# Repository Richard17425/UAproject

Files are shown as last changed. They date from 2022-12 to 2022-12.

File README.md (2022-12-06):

# **UAproject** (ReadOnly)
These are the projects I was responsible for when I was in University of Alberta, summer 2022. 
The projects this folder include are:

-  ## [**Cane**](Cane/scirobotics.abg6594_sm.pdf) 
-  ## [**Motion Sensor Glove**](Motion%20Sensor%20Glove/Instruction.pdf)
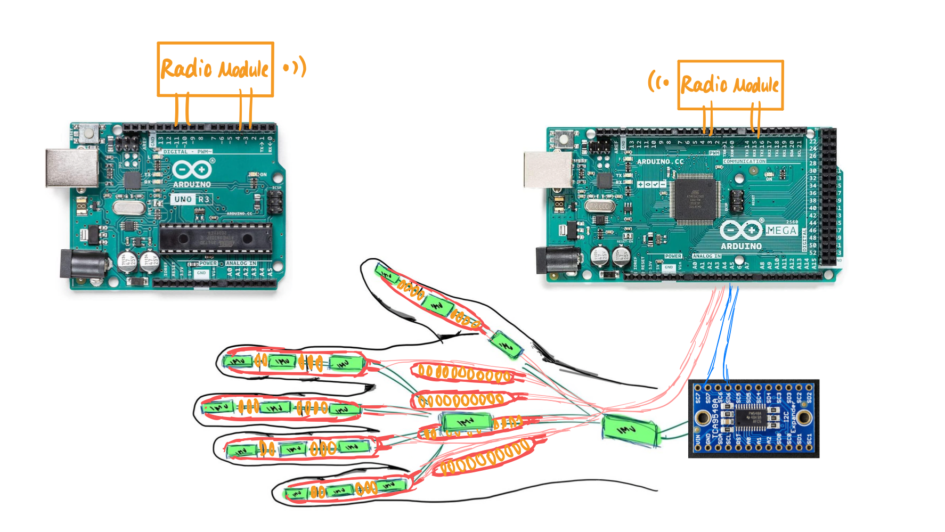
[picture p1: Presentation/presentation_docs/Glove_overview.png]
glove
  
-  ## [**Prosthetic Hand**](Prosthetic%20Hand/06_01_22_abstract-presentation.pdf)
hand

You can find details of these project in the folders.

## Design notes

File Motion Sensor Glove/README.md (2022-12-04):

# **Motion Sensor Glove**

This is the finnal vision of this project.So it will be much more simplified.

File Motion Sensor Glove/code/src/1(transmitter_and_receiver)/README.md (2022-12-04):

**Module 1**
====================================
This code contains transmitter and receiver codes
-----------------

    Make sure you have moved the *SparkFun_LSM9DS1_Arduino_Library folder* and the *RadioHead* into a libraries folder within your Arduino sketchbook or use the Library Manger to install.

- Receiver_Code_V2.0* should be uploaded to the Arduino Uno. Baud rate is **9 600**.

- *Receiver_Code_V2.0* should be uploaded to the Aduino Mega2560. Baud rate is **115 200**.

Author: richy70425@gmail.com

Original Creation Date: September, 2022

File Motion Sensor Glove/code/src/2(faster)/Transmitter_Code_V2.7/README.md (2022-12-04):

**Module 2**
====================================
This code contains only transmitter code, which means we connect the transmitter(Arduino Mega2560) to laptop directly.
-----------------

    Make sure you have moved the *SparkFun_LSM9DS1_Arduino_Library folder* and the *RadioHead* into a libraries folder within your Arduino sketchbook or use the Library Manger to install.

- *Transmitter_Code_V2.7* should be uploaded to the Arduino Uno. Baud rate is **2000 00**.

Author: richy70425@gmail.com

Original Creation Date: September, 2022

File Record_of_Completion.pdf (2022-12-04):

## Record of Completion

This certificate hereby acknowledges that

## Lab & Chemical Safety 2021

## Ruiqi Mao

has completed the course

July 13, 2022

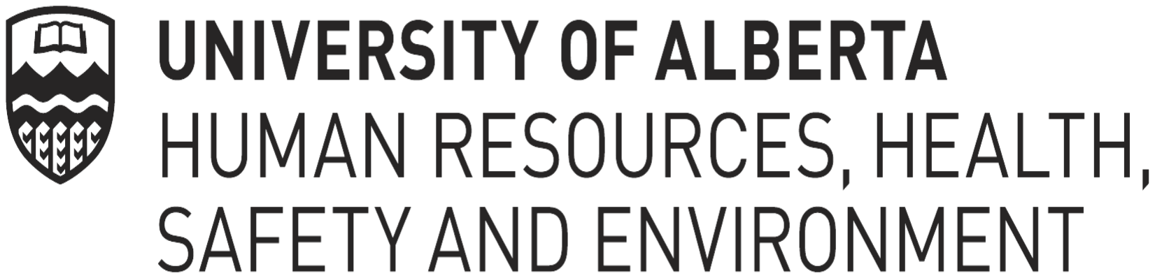
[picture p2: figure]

Philip Stack
Director, Health, Safety & Environment | 4lxVLtbr6s

Powered by TCPDF (www.tcpdf.org)

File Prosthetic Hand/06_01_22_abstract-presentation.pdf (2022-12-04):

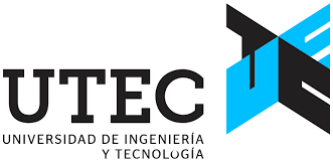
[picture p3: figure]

# DEVELOPMENT OF A LOW-COST

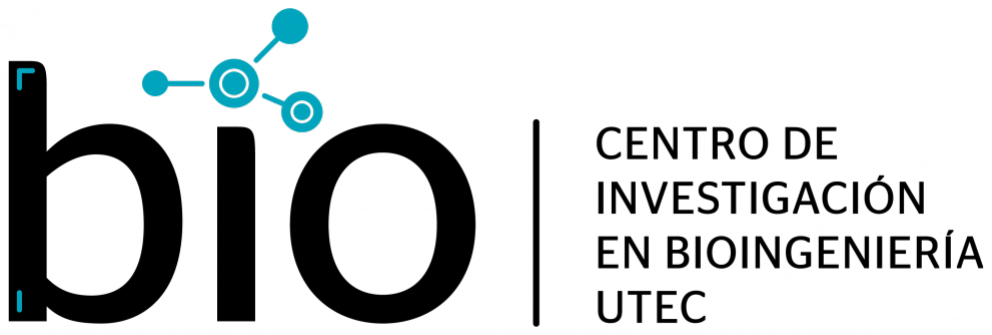
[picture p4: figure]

# LIGHTWEIGHT EMG-CONTROLLED TRANSRADIAL

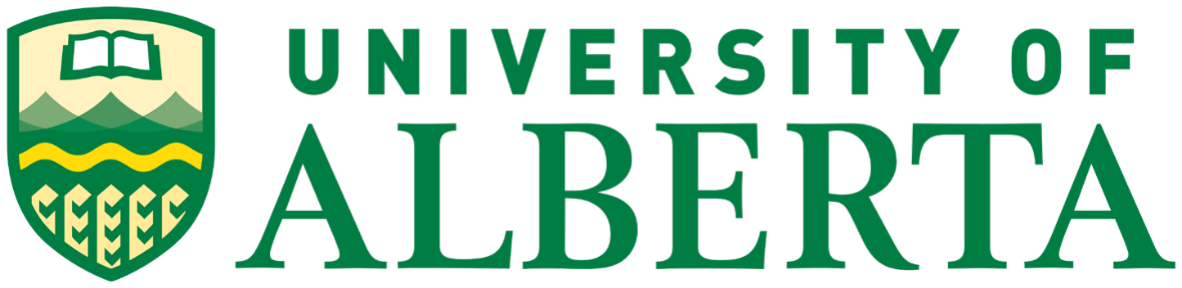
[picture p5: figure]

# PROSTHESIS

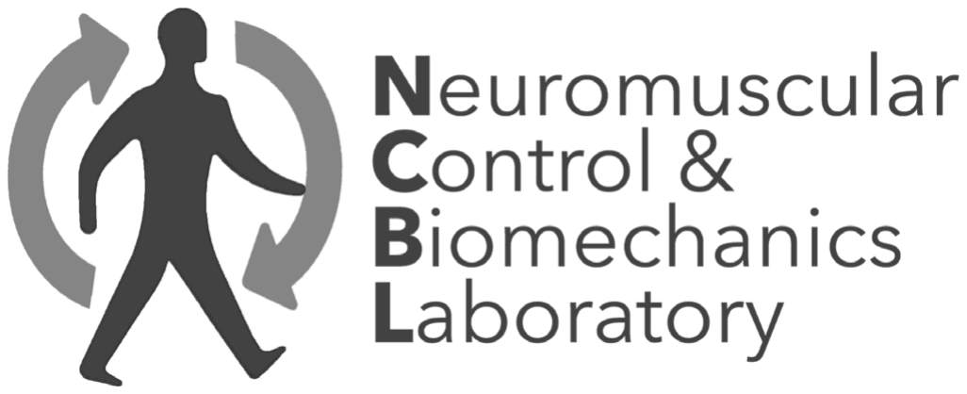
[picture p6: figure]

# Leonardo Torres Oscar Ramos, PhD | Hossein Rouhani, PhD

# Motivation

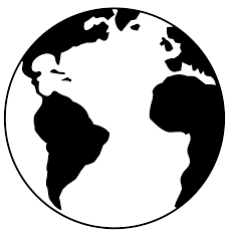
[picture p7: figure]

## 0.5% of population need orthotic and prosthetic services

### 35-40M of people

(WHO, 2017) [1]

## 85-95% of people in need of

an orthopedic device such as a prosthesis or orthosis, don’t have access to those
(WHO, 2017) [1]

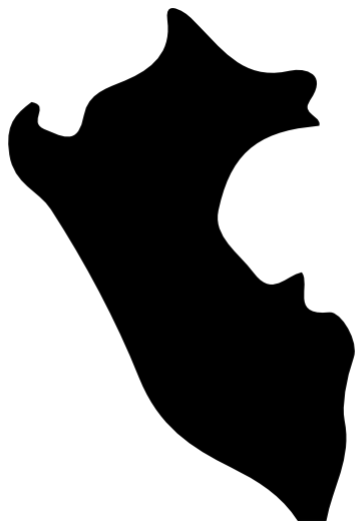
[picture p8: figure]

## 1.57% Peruvians with arm or leg disability

(National Census - INEI, 2017) [2]

## 0.001% Peruvians with locomotion disability use a prosthetic arm

(National Survey Specialized on Disability - INEI, 2012) [3]
2

# Motivation

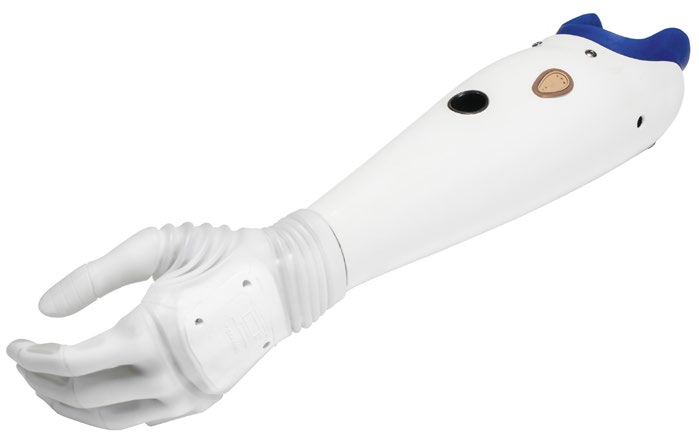
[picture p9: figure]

3

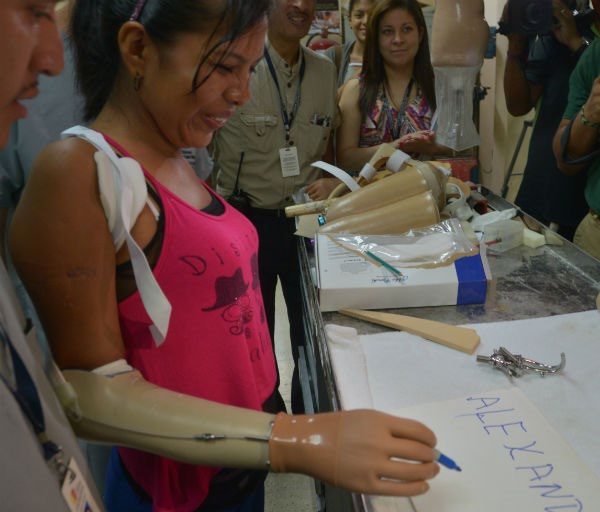
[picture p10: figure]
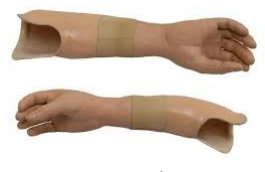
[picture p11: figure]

## Prosthesis from the National Rehabilitation Institute (INR), Peru

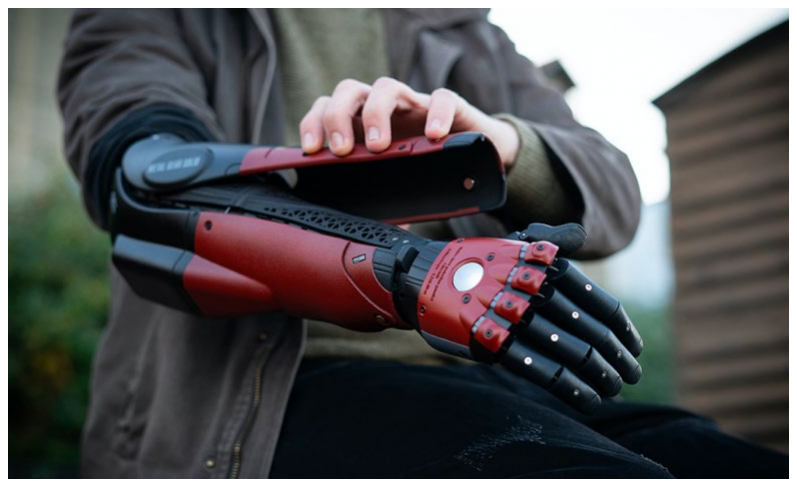
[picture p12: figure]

## Myoelectric Prosthesis from International Market

### Mechanical prosthesis Price: $ 1.500 USD [4]

### Aesthetic prosthesis Price: $ 1.000 USD [5]

### Hero Arm Prosthesis, Open Bionics. Price: $ 6.600 USD

[6]

### Michelangelo Hand

Prosthesis, Ottobock.

### Price: $ 60.000 USD

[6]

# Justification

4

## Accessibility: less cost of implementation

## Open source: easy replication by maker community

## Functional: actuation system with myoelectric signal

## Scalability: fast updates with software

# Objectives

5

Design the anthropomorphic prosthesis with 3 degrees of freedom.

Design the electronic system of the prosthesis.

## Develop the control system of the prosthesis using myoelectric signal

classification.

## Build the prototype of the upper limb prosthesis from the designed

components.

Functionally validate the implemented prosthesis.

# Mechanical design: SolidWorks assembly

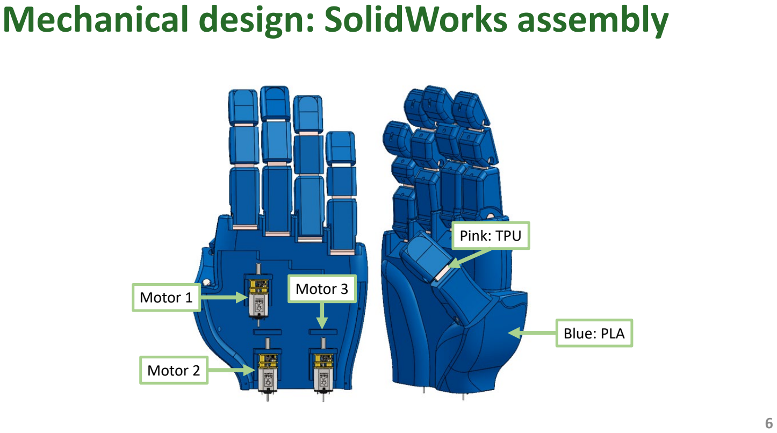
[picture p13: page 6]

6

### Motor 1

### Motor 2

### Motor 3

### Pink: TPU

### Blue: PLA

# Mechanical design: based on anthropometric data

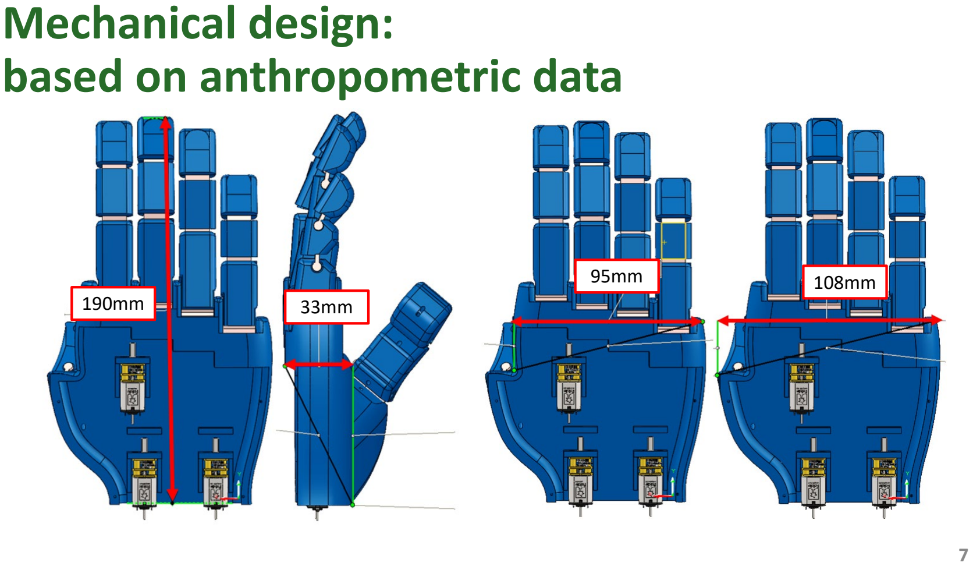
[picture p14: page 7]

7

190mm | 33mm
95mm | 108mm

# Electronic system: circuit diagram

8

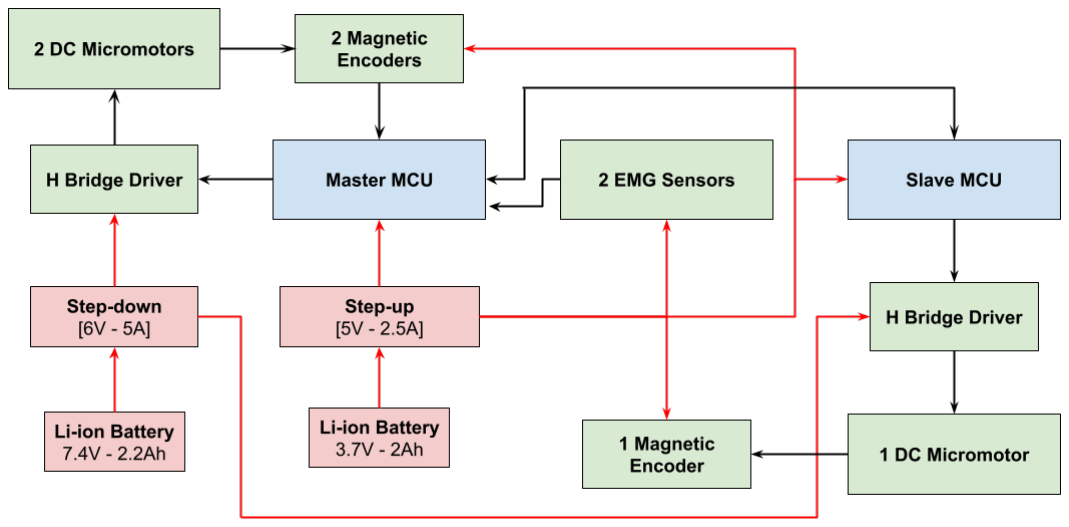
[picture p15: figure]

## LEGEND

### Microcontroller

### Power Supply

### Sensor/Actuator

# Electronic system: final circuit

## Printed circuit board (PCB) assembly results:

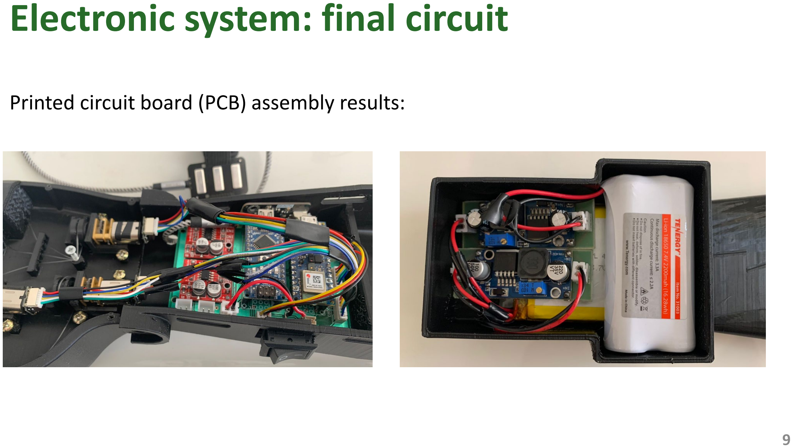
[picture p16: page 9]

9

# EMG signal: Processing Algorithm

10

### Data collection of EMG sensor

### Data filtering

### Data storage for 0.5s

### Calculation of average data

Changes state | Remains in the same state Threshold exceeded?
Yes | No

# Control System: Block diagram

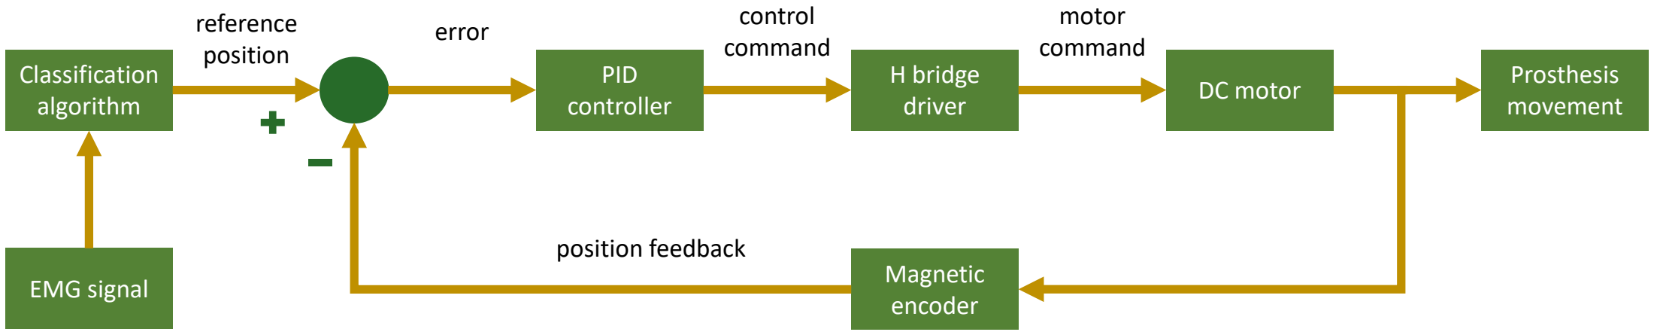
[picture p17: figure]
EMG signal; Classification algorithm; PID controller; H bridge; driver; DC motor; Prosthesis; movement; reference position; error; control command; motor command; Magnetic encoder; position feedback

11

# Fabrication: final cost of prosthesis

12

Service | Quantity | Unit Price | Cost
3D printing | 65 hours | $ 2.00 | $ 130.00
PCB printing | 1 unit | $ 35.00 | $ 35.00
| | Total | $ 165.00
Material costs | $ 274.75
Service costs | $ 165.00
Total | ≈ $ 440.00

# Weight of the prosthesis

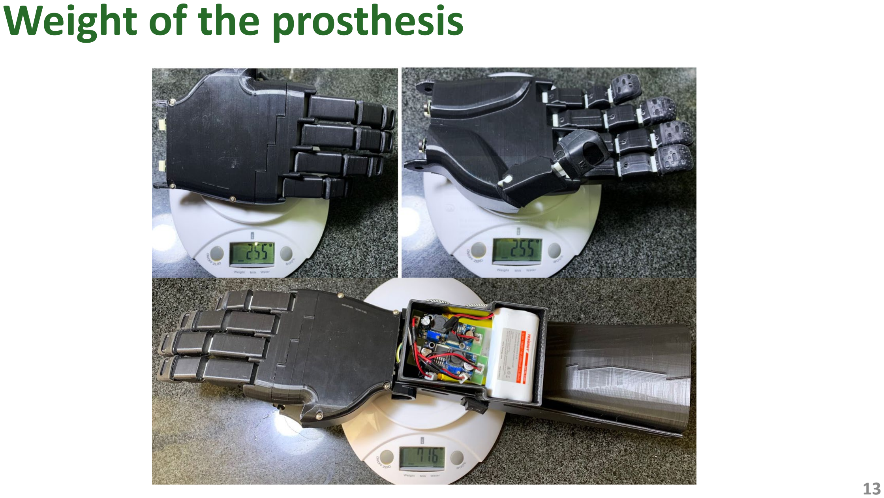
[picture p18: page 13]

13

Figure 18. Weight of the assembled prosthetic hand.

# Prosthetic hand movement

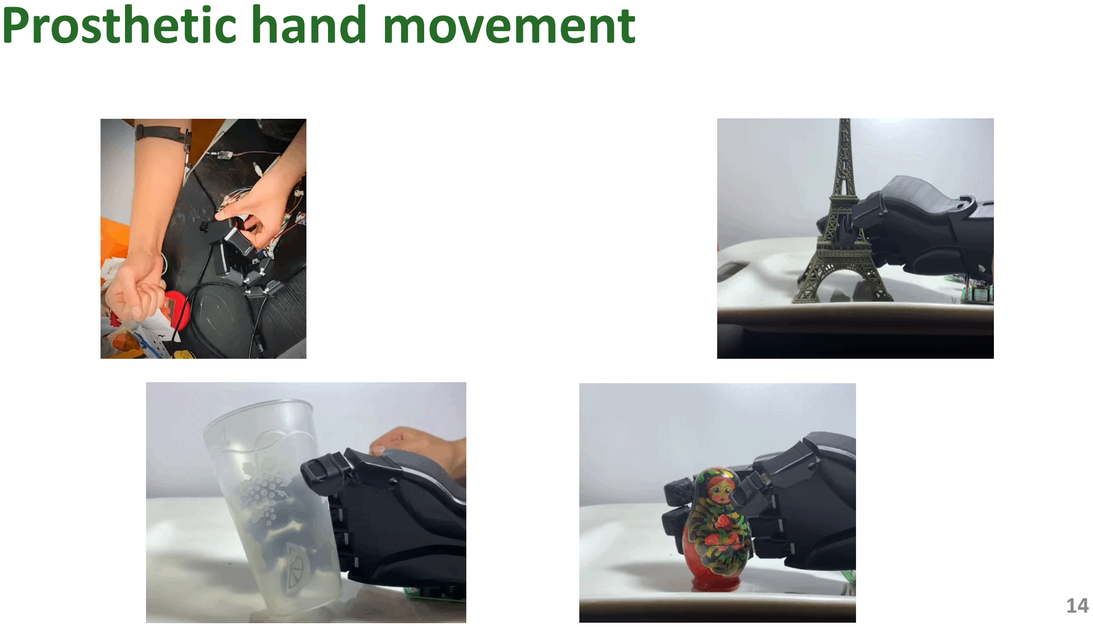
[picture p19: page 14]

14

# Conclusion:

- CAD design of the anthropomorphic prosthesis with 3 degrees of freedom.

## - Hand design similar to the average anthropometric measurements of the Latin

American database.
- Prototyping: 3D Printing time of 65 hours.
- Final implementation cost for materials and service was $440.
- Total weight within the limits initially proposed: 716 grams.

15

# Bibliography

16

[1] Organización Mundial de la Salud, “Normas de Ortoprostésica Parte 1: Normas,” 2017.
[2] Instituto Nacional de Estadística e Informática del Perú (INEI), “Perfil sociodemográfico de la población con discapacidad, 2017,” 2017.
[3] INEI, “Primera Encuesta Nacional Especializada sobre Discapacidad 2012,” 2012.
[4] Instituto Nacional de Rehabilitación, Resolución Directoral 122-2015-SA-DG-INR. Perú, 2015.
[5] Instituto Nacional de Rehabilitación, Resolución Directoral 406-2015-SA-DG-INR. 2015.
[6] A. Calado, F. Soares, and D. Matos, “A Review on Commercially Available Anthropomorphic Myoelectric Prosthetic Hands, Pattern-Recognition-Based Microcontrollers and sEMG Sensors used for Prosthetic Control,” 19th IEEE Int. Conf. Auton. Robot Syst. Compet. ICARSC 2019, 2019, doi: 10.1109/ICARSC.2019.8733629.
[7] Open Bionics, “Meet the Hero Arm – a prosthetic arm for adults and childern”, 2021. https://openbionics.com/hero-arm/ (accessed Aug. 5, 2021).
[8] R. Ávila, P. Lilia, and G. Elvia, Dimensiones antropométricas de población latinoamericana. 2007.
[9] O. Binvignat, A. Almagià, P. Lizana, and E. Olave, “Aspectos Biométricos de la Mano de Individuos Chilenos,” Int. J. Morphol., vol. 30, no. 2, pp. 599–606, 2012, doi: 10.4067/s0717-95022012000200040.
[10] B. Hirt, H. Seyhan, M. Wagner, and R. Zumhasch, Hand and Wrist Anatomy and Biomechanics: A Comprehensive Guide. Stuttgart: Thieme, 2017.

# Follow us on:

# THANK YOU !

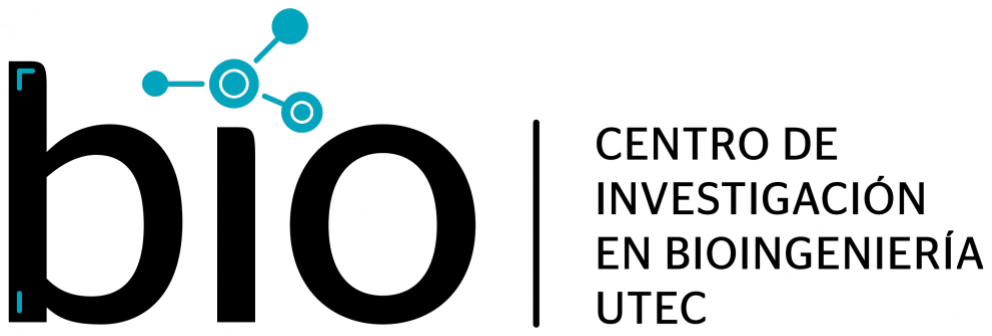
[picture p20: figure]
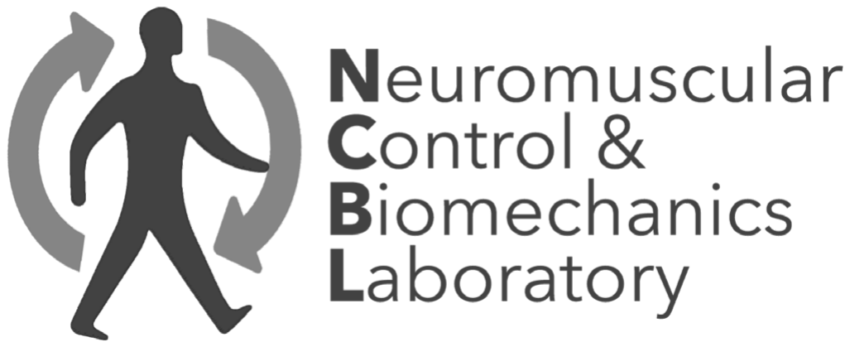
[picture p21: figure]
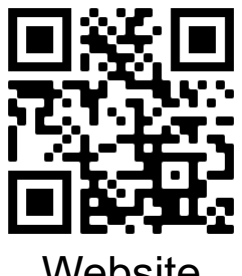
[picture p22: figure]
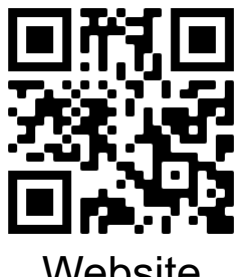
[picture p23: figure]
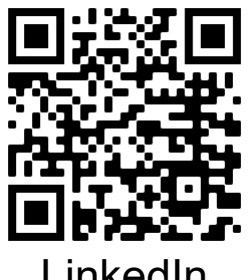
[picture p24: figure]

Website | LinkedIn | Website

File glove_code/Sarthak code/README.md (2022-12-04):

# These are Sarthak‘s codes
Version 2.0 is my improved code

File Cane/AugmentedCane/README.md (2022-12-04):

# AugmentedCane


The Augmented Cane project improves the mobility of people with impaired vision by using cutting-edge robotics. Read the full research paper: https://www.science.org/doi/10.1126/scirobotics.abg6594

If you use a part of this project please cite our work: P. Slade, A. Tambe, M. J. Kochenderfer, Multimodal sensing and intuitive steering assistance improve navigation and mobility for people with impaired vision. Sci. Robot. 6, eabg6594 (2021).

The Augmented Cane project is completely open-source. To build your own copy check out the cane_assembly document with instructions on replicating the device. The image of the Raspberry Pi used is available in a separate repository due to its size: https://doi.org/10.5281/zenodo.5508346

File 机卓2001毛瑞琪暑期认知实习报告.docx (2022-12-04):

2022暑期认知实习报告

机卓2001毛瑞琪

今年暑假，我有幸能参加由中国留学基金委资助的与加拿大阿尔伯塔大学的为期三个月的暑期实习项目。

阿尔伯塔大学（University of Alberta），简称“UA”，始建于1908年，是坐落于加拿大阿尔伯塔省会埃德蒙顿的一所世界著名研究型大学，是加拿大U15研究型大学联盟创始成员、世界大学联盟成员以及世界能源大学联盟成员。阿尔伯塔大学是加拿大最大的研究型大学之一，在地球科学，石油化工、化学、商学、农学、生物医学等学科最为著名。阿尔伯塔大学校友包含第16任加拿大总理，三位诺贝尔奖得主（包括2020年诺贝尔生理学医学奖得主霍顿 ），75位罗德学者（总数居世界名牌大学前列），141位加拿大皇家学会成员，111位加拿大首席研究教授。

阿尔伯塔大学的人工智能专业在全球居于领先地位，全球顶级计算机科学机构排名CSRankings 2010-2020年度人工智能领域世界排名第37名，其中人工智能和机器学习世界第6名。强化学习之父Rich Sutton、以及Alpha Go的主要作者大卫·席尔瓦（David Silver）和黄士杰（Aja Huang）均来自阿尔伯塔大学。

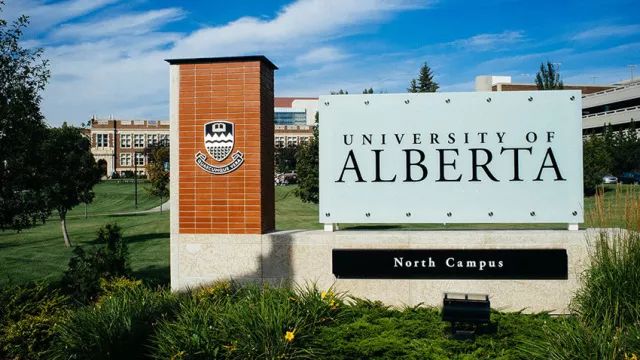
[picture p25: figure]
查看源图像

关于阿尔伯塔大学的机械工程系，教授告诉我，这里主要想要为学生提供在加拿大最大的机械工程系追求卓越、高质量教育的机会。学院的1,450名学生（1000 名本科生和450名研究生）在蓬勃发展和充满活力的环境中学习，强调扎实的学术和良好的实践技能。机械学院还提供合作的本科课程（包括生物医学合作选项），以及工程硕士、理学硕士和博士研究生课程。

我还了解到，阿尔伯塔大学的学生有许多丰富的研究和课外机会：从本科生研究计划到许多专注于机器人技术、自主飞行、F-1 赛车、火箭、生物力学、卫星、永续农业、氢动力汽车和许多其他领域的学生俱乐部团体，每个学生都会对某些事情或者某项研究充满热情。

在侧边栏查询中搜索

我从前觉得自己总是很忙，有各种各样学业的任务需要完成，一直在学习着、了解着工程与机械相关的内容，查论文写报告做展示，但在投入到实际中去探索与了解的时间确实有些捉襟见肘。真的说到未来科研或者工作会需要做些什么，我自己很难给出明确的回答。直到这次出来实习，才开始考虑一些之前没有重视的问题，开始真正去思考关于自己未来的事情。

首先是这边的科研，阿尔伯塔大学机械工程学院的主要研究大概可以分为下面四个方面：

设计理论与方法论：协作和交互方法；设计内容和流程管理；跨学科设计整合与优化；DFX; 功能建模；以用户为中心的设计建模。

设计和制造信息学：计算机辅助设计（CAD）；计算机辅助制造（CAM）；消费品创新；工程信息集成；工业管理信息学；知识工程；坚固的设计；产品生命周期管理；智能规划。

制造与生产系统设计与自动化：添加剂制造; 自动化和机器人技术；计算机数控（CNC）；柔性制造系统（FMS）；混合制造；STEP-NC，异种材料的激光焊接；物理、功能、工具和生产模型集成；和制造工装设计。

制造工艺优化：组装/拆卸；企业资源计划（ERP）系统的定制和开发；制造业供应链的扩展；人机协作；工业信息交互的互操作性；精益制造；工程设计、制造和生产过程的优化；制造质量保证；制造过程的模拟和分析；公差分析和分配。

因为这次的暑期实习项目是导师制的，所以我的大部分工作都是在完成导师的给我分配的项目任务。刚开始进入课题项目的时候我还只是做一些比较简单基础的工作，像是采购完成项目需要用到的一些材料跟零件，焊一些传感器的引脚以及做一些调试测试，作为志愿者完成实验室师兄师姐们的课题实验。这一系列的工作和任务让我对这边的科研环境与氛围有了基本的了解——一位在这边做科研的中国博士师兄告诉我，这边实验室的工作氛围比较自由，可以自己安排每天在实验室的工作时间，当然也可以居家办公，这就给了我们很高的自主安排的空间。当然，随之而来的也是对自己自律性的考验。我觉得这样安排的好处在于可以让那些真正想做科研的研究生们可以有一个安静的环境和氛围来做研究，每天自己计划要进行的任务和实验，不需要为刻板的工时去被迫强制性地工作，更多让人感受到的是在为自己打工。


后来我在实验室做的工作逐渐越来越多，也有了自己的主线任务。一个是拓展手的项目，原理是人在伸展或者握紧手的时候，实际上手臂上的韧带是会有相应的动作的，根据传感器得到的韧带的起伏数据，单片机就能知道我们手掌五指所要进行的动作是握拳或者是松手。这个项目的初衷是想要帮助那些残障人士在日常生活中能够像正常人一样拿东西，做一些简单的动作。为了保证假肢的制造精度和尽量还原出人手的各个关节形态，整个假手的制造主要是3D打印加上一些拼装，手指的韧带采用的是TPU材料，更加具有韧性。五个手指分别用三个电机来驱动，当单片机对传感器获得的手部的信号分析处理后，会向电机做出相应的指令，从而电机转动拉动绳子，实现手指的弯曲。整个原理其实很简单，但实现的过程却充满了艰辛和坎坷。由于要获得手部韧带准确的动作信息，传感器的位置跟方向都很讲究。所以对医学几乎一无所知的我在这上面吃了大亏。我上网到处搜索手臂韧带的相关信息，看了一些相关的论文研究，还加以自己的推测，一次又一次尝试，调整传感器在手臂上的粘贴位置，最终才让全部的四个传感器处在了正确的位置。经过后来又很多次的调试，才终于让整个的拓展手正常工作了起来。

这个项目我收获最大的除了一些经验，也让我学会在遇到困难的时候不畏惧不浮躁—如果只是抱怨是解决不了问题的，只有亲手去做，认真去思考才能真正解决问题。还有就是要细心。在调试电机的时候，我发现有一个电机总是对单片机发出的信号无动于衷，我反复检查了代码与连线，最后发现居然是驱动板上的GND没有接上。这些小错误都耗费了我很多的时间，也是给我了很好的教训。毕竟这还只是一个小项目，要是以后到了真正工程上的大项目，这样的粗心可是折腾不起的。因为自己的一个小小的粗心可能带来的是数以万计的损失和浪费，这真的是一个工程师要绝对避免的。


同时，关于这个项目，教授还让我思考是否还能对这个假肢做出一些改进，是否能够站在环境保护和可持续发展的角度，思考机械设计制造及其自动化领域工程实践的可持续发展性，并评价产品周期中可能对人类和环境造成的损害和隐患。这是我在开始时没有考虑到的，就像整个手臂的制造为了方便，我选择了PLA的塑料，但是却没有考虑到这后面的成本和环保问题。是否能够有更好的材料来进行替代，是否可以降低整个假肢的生产制造成本，我觉得这都是一个好的工程师在设计之初就应该考虑到的。我又想到原来在学校的时候听的院士的讲座上也提到了可持续发展的问题----我们国家人口多、自然资源短缺、经济基础和科技水平落后，只有节约资源、保护环境，才能实现社会和经济的良性循环，使各方面的发展能够持续有后劲。可持续发展要求我们 “能满足当代人的需要，又不对后代人满足其需要的能力构成危害的发展”。 它包括两个重要概念：一个是需要，尤其是世界各国人们的基本需要，应将此放在特别优先的地位来考虑；另一个是限制，技术状况和社会组织对环境满足眼前和将来需要的能力施加的限制。可持续发展的概念涵盖范围包括国际、区域、地方及特定界别的层面，是我们国家科学发展观的基本要求之一，也是当今世界关注的重点之一。原来总觉得这种事情仿佛是只出现在号召里，自己难能做些什么帮助，但确实仔细一想其实就在机械设计制造的过程中都有很多可以环保节能的可持续的设计和方法，有时候甚至是一个小小的改动或者改进，在大批量生产制造中都会产生举足轻重的作用。而且可持续发展更像是一种为人处世的哲学，它要求我们从注重眼前利益、局部利益的发展转向长期利益、整体利益的发展，需要我们拥有一种大局观和对未来的规划。


教授也告诉我，机械其实包含的领域很广，是一个多学科研究交叉互相融合的领域。一个好的机械工程师或者研究人员应该专注于系统、流程、机器、工具和生产设备的设计和开发，通过创造性的概念化、知识工程的工程化，找到最经济、最有效的方法，将想法转化为新的或更新的产品、流程或技术来满足社会和工业需求。这种研究工作通常需要考虑经济、安全、信息学以及环境、认知、文化、社会学甚至生理学问题，所以对我们的要求非常高。

教授虽然对于研究生的工作时间没有强制性的要求，可是对于我们的工作质量与成果却十分严格。每周，教授都安排师姐给我分配任务，师姐每天还会询问我的进度，如果有遇到困难或者需要就可以及时解决。教授一般出现在一周一次的组会上，有一次教授就师兄展示PPT上的一个点讨论了很久，因为觉得关于脑电波获取思路原理上没有讲得清楚正确而把师兄批评了一顿。还有一次，同样是交换在我们实验室进行项目实习的一位墨西哥的同学在进行最终的项目展示时，因为PPT里关于自己成果展示不够充分明显，导师也毫不留情地指出批评。但是尽管如此，我觉得难能可贵地是，教授依旧能跟我们打成一片。在八月初我们实验室的聚餐中，教授一手拿着汉堡，一边跟我们几个年轻的暑期实习生聊天。当时突然觉得将近半百的教授十分可爱、和蔼可亲。一起的一位大三的印度暑期交换生，因为在未来毕业选择继续读研的方向上依旧有一些疑惑和犹豫，向教授咨询。在问到未来在哪工作生活时，教授意味深长地说：其实当你觉得选择很困难的时候，答案其实很简单，因为要不是A要不是B，其实真正影响结果的，往往并不是选择本身，而是选择之后你做了什么，选择你心之所向的，然后就执着于此，将它变成最好的哪个选项。


再就是关于未来发展的一些想法。来了这边，真正开始潜下心来做一些事情以后才发现，自己真的是想的很多但是做的很少。很多时候都在犹豫在比较到底做哪一个是最好，但实际上只有真正出发去实践才会知道哪些选择是所谓正确的。所以出国也好，国内也一样，不管在哪里，认真做事才是真正关键重要的。甚至觉得自己对于所谓名校过去也有很过分的执着，好像非哪个学校上不可。可是我没有意识到，除了学校之外的东西，那是关于自己的。在哪个国家，哪个城市，哪个学校哪个导师哪个课题组，这是外在的环境，它们都是你的背景色，诚然，一定程度上这些背景很重要，但是除开这些以外，我们真正应该关注的，更是我们自己本身——因为我们自己的命运是掌握在自己手里的，只有它才是我们能实际改变的。

从前觉得自己做事都是有很强的目的性，而并不是真的纯粹因兴趣而朝着哪个方向努力，功利性往往很强，虽然这样让我也浅浅尝到了些甜头，但走着走着就发现在这样的驱动力下自己走的路越来越窄，因为这种目的性我并不认为是一种规划，而更像是成为了自己的一种人生执念或者说唯一目的似的行事方式。也许是因为之前在大一大二时主要学的也是些基础课程，我会难免把自己高中的那一套行事方式带到大学来，可真正的大学生活当然不应该是这样的。来到这边我才发现，一起的来这里参加暑期实习项目的来自中国各个高校的拔尖的同学们，他们对自己大学生涯的规划是多么的有条理，而且这些规划或者说是想法是自然而然地，根据自己的兴趣导向的。就拿一位香港大学生物医疗专业的同学为例，她大一下学期的时候就联系上了在深圳做研究的一位导师，大二进入课题组开始做研究，在上课的同时自己学习相关的知识完成项目任务，大二的暑假又来参加了加拿大Mitacs的暑期研究项目，她跟我讲到说：她向学校申请从大三开始做毕业设计，这样大四的时候就可以有更多的时间做项目，同时她也打算大三下学期的时候出国做科研，有了这些研究的经历，以及一路上积累的科研产出，在大四那年可以说她就已经硕果累累，仿佛申请海外的博士研究生就不过是顺其自然的事情。我听完真的感慨万分，也许真正优秀的人的计划让人看来就像是顺其自然的事情，而且更让我敬佩的是，她告诉我其实香港大学的课程并没有国内大学那么硬核，但有一个优点是比较自由灵活，所以她可以能够根据自己的时间来调整课程的安排。由衷地让我感到：原来有的时候我们需要的并不是有一手好牌，而是能够把自己有的牌打得最好。能够将自己所有的资源发挥到极致，这才是真正令人敬佩的。

这是我20岁以来第一次出国，还是第一次一个人出走这么远。在我在这边的快两个月的日子里，我觉得除了学术上的知识性的收获，更多的我觉得是作为人生路上如何做人、如何逐渐成为一个合格的大人的收获。这是比那些书面上的知识更为抽象却又最为宝贵的知识，也是我在这边非常宝贵的经历。从去年九月开始准备申请这次的暑期项目到后来面试再到护照签证的准备，从出国前的安排住宿接机到转机和办理入关，再到办置出租屋里的生活基本品，从第一次到实验室里当志愿者做测试，到后来自己一个人两个实验室呆上一整天做项目，从第一次开小组会听的云里雾里，到后来自己也可以在组会上发表自己的观点……感觉自己在不断面对挑战、克服困难，一步一步地拓宽自己的边界，不断提升自己的能力来适应这个新的环境，逐渐成为一个靠谱的大人，成为一个自己想要成为的人。

2022年8月25日

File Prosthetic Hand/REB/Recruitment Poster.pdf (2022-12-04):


••

••

••

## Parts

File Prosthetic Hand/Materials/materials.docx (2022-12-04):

Vibration motor:

- Link [5PCS 10x2mm Micro DC Vibrating Motor, DC 3V 80mA 11000±2500rpm Flat Coin Button-Type Mini Vibration Motor for Smart Cell Phone Pager Tablet(27m)]: https://www.amazon.ca/dp/B089NTLLWB/?coliid=I3SHLB6QTZHJKF&colid=19ZIG9ZNK2RJU&psc=1&ref_=lv_ov_lig_dp_it
- Description:
  - Rated voltage: 3.0V DC
  - Operating voltage range: 2.3-4.0V DC
  - Direction of rotation: CM (clockwise) or CCW (counterclockwise)
  - Rated speed: 11000 ± 2500rpm
  - Rated current: 80mA Max
  - Starting current: 120mA Max
  - Starting voltage: 2.3V DC Max
  - Insulation resistance: 100MΩ Min
  - Bottom deflection intensity: 9.8N
  - Mechanical noise: <50dB
  - Background noise: <28dB (at rated voltage)
  - Operating environment: -20~60, Ordinary humidity
  - Storage environment: -30~70, Ordinary humidity
  - Diameter: 10mm
  - Height: 2mm
  - Optional size: 20/27/30/34mm

Force Sensing Resistor:

- Link [2Pcs Thin Film Pressure Sensor, High Precise Force-Sensitive Resistor Force Sensor Pressure Sensor Resistance-Type Thin Film Pressure Sensor, Force Sensing Resistor]: https://www.amazon.ca/dp/B07T1CHY58/?coliid=I2BXVPN0XJKUDV&colid=19ZIG9ZNK2RJU&psc=1&ref_=lv_ov_lig_dp_it
- Description:
  - Model: RP-C10-ST
  - Thickness: 0.4 mm
  - Trigger force: 20 g, triggered when resistance is less than 200 kΩ by default
  - Pressure sensing range: 20 g ~ 2 kg
  - Pressure action mode: Static or dynamic (frequency within 10 Hz)
  - Non-trigger resistance: More than 10 MΩ
  - Activation time: less than 0.01 S
  - Operating temperature: -40 ℃ ~ +85 ℃
  - Lag: +10%, (RF+ - RF-)/FR+, 1000g force
  - Response time: < 10 ms
  - Drifting: <5%, 1Kg force static load 24H
  - Weight: 1g / 0.04oz (approx.)

Silicone Molding

- Link [LET'S RESIN Silicone Mold Making Kit Liquid Silicone Rubber Non-Toxic Translucent Clear Mold Making Silicone-Mixing Ratio 1:1-Molding Silicone for Resin Molds,Silicone Molds DIY Manual Making(21.16oz)]: https://www.amazon.ca/LETS-RESIN-Silicone-Making-Non-Toxic/dp/B07V5FFPWC/ref=pd_sbs_5/146-4764598-8827200?pd_rd_w=EHmp4&pf_rd_p=6b62794c-5c28-477c-b43d-0b3e13e4d3b5&pf_rd_r=6M10TPN63P1DRJPE3RWP&pd_rd_r=4c0c2dec-ce9d-476c-a0fa-1ec1a55e39f8&pd_rd_wg=2kSPs&pd_rd_i=B07V5FFPWC&psc=1
- Description:
  - EASY MIXING & POURING: This silicone molds making kit includes part A and part B, the mix ratio is 1:1 by weight. Pour the Part A and Part B together, then stir the silicone rubber for 5 minutes, make sure to stir the liquid rubber mixture thoroughly for better results. The working time is 5 minutes at room temperature.
  - NO BUBBLES: The bubbles of liquid silicone will automatically disappear within 2 hours; no vacuum degassing is necessary. The working time of making mold kit is 5 minutes at room temperature and the complete cure time is at least 12 hours at room temperature, it varies on your mold size and thickness. If it's s little sticky, please extend the curing time of silicone rubber

Silicone Resin Tool Kit

- Link [Silicone Resin Measuring Cups Tool Kit, Reusable Nonstick Silicone Mat, 100ml Silicone Measuring Cups, Finger Cots, Resin Mix Cup, Stir Stick Pipette (29PCS)]: https://www.amazon.ca/dp/B08V515WJF/ref=sspa_dk_detail_2?pd_rd_i=B08V515WJF&pd_rd_w=9Zozb&pf_rd_p=a2b32c5b-02b0-4273-a3c7-c6bfabb067a2&pd_rd_wg=7xj4c&pf_rd_r=XPAAMCDKMT3XWRBMZHWA&pd_rd_r=e0316371-c8f5-4904-a0ce-ecf62129b311&s=kitchen&spLa=ZW5jcnlwdGVkUXVhbGlmaWVyPUExSkpIRVlYUU5MUzg4JmVuY3J5cHRlZElkPUEwNzUzOTc2Mk5HUTdCU0JKQzZZUCZlbmNyeXB0ZWRBZElkPUEwOTAzNTU3MzVMTFpEOE5WMEtKUCZ3aWRnZXROYW1lPXNwX2RldGFpbCZhY3Rpb249Y2xpY2tSZWRpcmVjdCZkb05vdExvZ0NsaWNrPXRydWU&th=1 (https://www.amazon.ca/dp/B08V515WJF?s=kitchen)
- Description:
  - 1Pcs Reusable Nonstick Silicone Mat,
  - 2Pcs 100ml Silicone Measuring Cups,
  - 10Pcs Finger Cots,
  - 4Pcs Resin Mix Cup,
  - 10Pcs Stir Stick Pipette,
  - 2Pcs Mixing Sticks

Potentiometers

- Link [Cylewet 6Pcs B2K B5K B10K B20K B50K B100K Ohm Knurled Shaft Linear Rotary Taper Potentiometer with Rotary Knob Cap for Arduino (Pack of 6) CLT1066]: https://www.amazon.ca/Cylewet-Knurled-Potentiometer-Arduino-CLT1066/dp/B07DFHXCZZ/ref=sr_1_1?dd=c04fGJKjKTLM_GOB3i0bXQ%2C%2C&keywords=potentiometer&qid=1644095990&refinements=p_90%3A11828088011&rnid=11828086011&sprefix=potent%2Caps%2C128&sr=8-1
- Description:
  - Resistance Value: 2K/ 5K/ 10K/ 20K/ 50K/ 100K Ohm
  - Adjustment Type: top adjustment; Type: single linear (Type B); Features: knurled shaft
  - Diameter of Shaft: 6mm/0.23in; Length of Shaft: 15mm/ 0.59in
  - Rotary Knob Cap: 15mm/ 0.59in (Diameter); 17mm/ 0.67in(Height); 6mm/ 0.24in(inner diameter)
  - Material: metal

Diodes

- Link [10V 200Pcs Diodes Box Set, 1N4001~1N5819 Zener Diode Combination Electronic Kit, Germanium Diode Kit with Transparent Box]: https://www.amazon.ca/Regulator-Assortment-Electronic-1N4001-1N4007-1N5817-1N5819/dp/B07CJMBMJS/ref=sr_1_3?crid=20YUJ66D5N0EQ&dd=c04fGJKjKTLM_GOB3i0bXQ%2C%2C&keywords=diode&qid=1644096042&refinements=p_90%3A11828088011&rnid=11828086011&sprefix=diode%2Caps%2C388&sr=8-3
- Description:
  - EXCELLENT PERFORMANCE: These diodes are low leakage and forward pressure drop, low power consumption, high efficiency.
  - 10 VALUE 200 PCS: 1N4001, 1N4002, 1N4003, 1N4004, 1N4005, 1N4006, 1N4007, 1N5817, 1N5818, 1N5819 each 20pcs diode box set.
  - APPLICABLE CROWD: The germanium diode for electronic professionals or enthusiasts, these are all kinds of diodes.
  - SCOPE OF APPLICATION: The capacitor kit is convenient for DIY and maintenance equipment and electrical appliances for home, office and industry.
  - WITH TRANSPARENT BOX: All diodes are packed correctly and placed in a transparent box for classification for convenient storage. There is a label on the box, so you can easily determine the type of diode you need.

Single Core Copper Wire

- Link [TUOFENG 22 awg Solid Wire-Solid Wire Kit-6 Different Colored 30 Feet/9M spools 22 Gauge Jumper Wire- Hook up Wire Kit]: https://www.amazon.ca/TUOFENG-Wire-Solid-Different-Colored-spools/dp/B086WF1WD1/ref=sr_1_16?crid=JWHL31OTYQ8E&keywords=copper+wire+tuofeng&qid=1646075488&sprefix=copper+wire+tuofeng%2Caps%2C107&sr=8-16
- Description:
  - Conductor AWG: 22
  - Conductor Material: Tinned Copper
  - Conductor Construction: Solid 1×0.65±0.008mm²
  - Insulation: PVC(Polyvinylchloride)
  - Over Dia.: 1.55±0.1mm
  - Temperature Rating: -40 degrees C to 80 degrees C.
  - Rated Voltage: 300V
  - FLAME TEST: VW-1
  - Packaging: 6 different colored 30 Feet spools

Dupont Connector Kit

- Link [Hilitchi 635 Pcs 40 Pin 2.54mm Pitch Single Row Pin Headers, Connector Housing Female, Male/Female Pin Kit for Dupont Wire Connectors]: https://www.amazon.ca/Hilitchi-2-54mm-Headers-Connector-Housing/dp/B014YTPFT8/ref=sr_1_6?crid=1QENBOG6N473F&keywords=wire+ferrule+arduino&qid=1645569293&s=industrial&sprefix=wire+ferrule+arduino%2Cindustrial%2C99&sr=1-6
- Description:
  - 2.54mm 1x1P Connector Housing Female x 20Pcs
  - 2.54mm 1x2P Connector Housing Female x 20Pcs
  - 2.54mm 1x3P Connector Housing Female x 20Pcs
  - 2.54mm 1x4P Connector Housing Female x 20Pcs
  - 2.54mm 1x5P Connector Housing Female x 20Pcs
  - 2.54mm 1x6P Connector Housing Female x 20Pcs
  - 2.54mm 1x7P Connector Housing Female x 20Pcs
  - 2.54mm 1x8P Connector Housing Female x 20Pcs
  - 2.54mm 1x9P Connector Housing Female x 15Pcs
  - 2.54mm 1x10P Connector Housing Female x 20Pcs
  - Jumper Wire Cable Female Pin Connector x 210Pcs
  - Jumper Wire Cable Male Pin Connector x 210Pcs
  - 10Pcs x 40 Pin 2.54mm Single Row Male Header for Arduino Prototype Shield.
  - 10Pcs x 40 Pin 2.54mm Pitch Single Row Right Angle PCB Pin Headers.

Crimping Tool

- Link [Hilitchi Professional Pin Crimping Tool 2.54mm 3.96mm 28-18awg 0.1-1.0mm² for Dupont Terminals with Wire-Electrode Cutting Die Insulated Terminal Crimper/Stripper/Cutter Tool]: https://www.amazon.ca/Hilitchi-Professional-0-1-1-0mm%C2%B2-Terminals-Wire-electrode/dp/B016B39EPQ/ref=pd_bxgy_img_1/146-4764598-8827200?pd_rd_w=uO75q&pf_rd_p=19eafb8a-881a-44bb-9725-85a79b8c53d4&pf_rd_r=D7KF2RQDFDDB8DJPDPJX&pd_rd_r=16ccfc79-4ce8-41d8-981e-8eace70878f2&pd_rd_wg=Fpe3r&pd_rd_i=B016B39EPQ&psc=1
- Description:
  - AWG: 28-18
  - 0.1-1.0m㎡
  - For 2.54mm 3.96mm KF2510 connector
  - Wire-electrode cutting die sets promise a high-precision crimping result.
  - Length: 190mm/7.4inch
  - Weight: 384g/13.5oz

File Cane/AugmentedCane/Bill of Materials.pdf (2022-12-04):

Number | Part Name | Vendor | Quantity | Cost
1 | Raspberry Pi 4b+ (4 GB) | Adafruit | 1 | $55.00
2 | RPLidar A1 | Amazon | 1 | $99.99
3 | Motor | Pololu | 1 | $19.95
4 | GPS Breakout | Adafruit | 1 | $39.95
5 | NXP IMU | Adafruit | 1 | $14.95
6 | RPi Camera | Adafruit | 1 | $29.95
7 | RPi Camera Cable | Adafruit | 1 | $2.95
8 | Pi Cobbler Breakout | Adafruit | 1 | $6.95
9 | Protohat | Adafruit | 1 | $4.95
10 | GPS Antenna | Adafruit | 1 | $14.95
11 | Micro SD Card | Amazon | 1 | $6.90
12 | LiPo Battery | Amazon | 1 | $13.00
13 | LiPo Charger | Amazon | 1 | $12.00
14 | USB cable | Adafruit | 1 | $2.95
15 | Rechargeable Battery | Amazon | 1 | $12.50
17 | Motor Driver | Adafruit | 1 | $7.50
18 | Pi Case | Amazon | 1 | $18.99
19 | White Cane | Amazon | 1 | $17.00
20 | Ear Buds | Amazon | 1 | $39.99
21 | 4mm shaft | Amazon | 1 | $7.99
22 | Omniwheel | Robotshop | 1 | $13.50
23 | Aluminum mounting hub | Robotshop | 2 | $6.21

Shipping | Total Cost | Link
$0.00 | $55.00 | https://www.adafruit.com/product/4296
$0.00 | $99.99 | https://www.amazon.com/Slamtec-RPLIDAR-Scanning-Avoidance-Navig
$0.00 | $19.95 | https://www.pololu.com/product/3225
$0.00 | $39.95 | https://www.adafruit.com/product/746
$0.00 | $14.95 | https://www.adafruit.com/product/3463
$0.00 | $29.95 | https://www.adafruit.com/product/3099
$0.00 | $2.95 | https://www.adafruit.com/product/1731
$0.00 | $6.95 | https://www.adafruit.com/product/1754
$0.00 | $4.95 | https://www.adafruit.com/product/2310
$0.00 | $14.95 | https://www.adafruit.com/product/960
$0.00 | $6.90 | https://www.amazon.com/Sandisk-Ultra-Micro-UHS-I-Adapter/dp/B073K
$0.00 | $13.00 | https://www.amazon.com/dp/B072PPRPRN/ref=sspa_dk_detail_2?psc=
$0.00 | $12.00 | https://www.amazon.com/Blomiky-Charger-11-1V-Balance-Battery/dp/B0
$0.00 | $2.95 | https://www.adafruit.com/product/4472
$0.00 | $12.50 | https://www.amazon.com/gp/product/B07MS1B8KQ/ref=ppx_yo_dt_b_as
$0.00 | $7.50 | https://www.adafruit.com/product/3190
$0.00 | $18.99 | https://www.amazon.com/Miuzei-Raspberry-HDMI-Micro-Aluminum-Inclu
$0.00 | $17.00 | https://www.amazon.com/Drive-Medical-Deluxe-Folding-Reflective/dp/B0
$0.00 | $39.99 | https://www.amazon.ca/Ergonomic-Headphones-APEKX-Waterproof-Su
$0.00 | $7.99 | https://www.amazon.com/Sutemribor-100mm-Straight-Helicopter-Airplan
$0.00 | $13.50 | https://www.robotshop.com/en/60mm-aluminum-omni-wheel.html
$0.00 | $12.42 | https://www.robotshop.com/en/4mm-aluminum-mounting-hub-60mm-om
TOTAL: | $454.33

gation/dp/B07TJW5SXF/ref=asc_df_B07TJW5SXF/?tag=hyprod-20&linkCode=df0&hvadid=385584089652&h

14CVB/ref=sxts_sxwds-bia-wc-nc-drs1_0?cv_ct_cx=16gb+sd&dchild=1&keywords=16gb+sd&pd_rd_i=B073K 1&pd_rd_i=B072PPRPRN&pd_rd_w=CCMt1&pf_rd_p=8a8f3917-7900-4ce8-ad90-adf0d53c0985&pd_rd_wg= 072K5LHGM/ref=sr_1_4?dchild=1&keywords=3s+lipo+charger&qid=1609976623&s=toys-and-games&sr=1-4

uded/dp/B07VX2WDHM/ref=sr_1_2_sspa?dchild=1&keywords=raspberry+pi+4+clear+case+fan&qid=160997

upporting/dp/B07XFMHQDP/ref=asc_df_B07XFMHQDP?tag=bingshopdesk-20&linkCode=df0&hvadid=80608 ne/dp/B07FYTQWDC/ref=sr_1_3?dchild=1&keywords=4mm+metal+shaft&qid=1611780543&sr=8-3 hvpos=&hvnetw=g&hvrand=17825053878959676056&hvpone=&hvptwo=&hvqmt=&hvdev=c&hvdvcmdl=&hvlo

K14CVB&pd_rd_r=4dc1bcc8-931d-43bc-913c-f218adc8df22&pd_rd_w=8coqJ&pd_rd_wg=ZjKYy&pf_rd_p=a6 =JfmBu&pf_rd_r=5Z930B0KXCTS9DHAZXDF&pd_rd_r=074eab42-6ba6-11e9-b12e-253105b62179

77011&sr=8-2-spons&psc=1&spLa=ZW5jcnlwdGVkUXVhbGlmaWVyPUFJOEdCUDhLR081QTEmZW5jcnlwd

8037718079&hvnetw=o&hvqmt=e&hvbmt=be&hvdev=c&hvlocint=&hvlocphy=&hvtargid=pla-45842075837910 ocint=&hvlocphy=9031968&hvtargid=pla-833793200531&psc=1&tag=&ref=&adgrpid=76780761017&hvpone=

64002b9-9c26-4361-b8a1-b0f5a4835670&pf_rd_r=K52WK63N5JQZFSEVDN2R&psc=1&qid=1609976431&s

dGVkSWQ9QTAwMjA0NzgyOVFLR1hSRzVMWEdGJmVuY3J5cHRlZEFkSWQ9QTA3Mjk2MjcxVE9LRlU0Qz

=&hvptwo=&hvadid=385584089652&hvpos=&hvnetw=g&hvrand=17825053878959676056&hvqmt=&hvdev=c

zY0TTQwJndpZGdldE5hbWU9c3BfYXRmJmFjdGlvbj1jbGlja1JlZGlyZWN0JmRvTm90TG9nQ2xpY2s9dHJ1Z c&hvdvcmdl=&hvlocint=&hvlocphy=9031968&hvtargid=pla-833793200531

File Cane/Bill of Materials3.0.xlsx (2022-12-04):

Number | Part Name | Vendor | Quantity | Cost | Shipping | Total Cost | Link
1 | RPLidar A1 | Amazon | 1 | $139.99 | $0.00 | $139.99 | Slamtec RPLIDAR A1 2D 360 Degree 12 Meters Scanning Radius LIDAR Sensor Scanner for Bstacle Avoidance and Navigation of Robots : Amazon.ca: Electronics (https://www.amazon.ca/Slamtec-RPLIDAR-Scanning-Avoidance-Navigation/dp/B07TJW5SXF)
2 | Motor(12V 200rpm) | Amazon | 1 | $17.03 | $0.00 | $17.03 | DC12V 200RPM Gear Box Reversible High Torque Reduction Electric Motor, DC Motor, Outer Diameter 20MM : Amazon.ca: Tools & Home Improvement (https://www.amazon.ca/dp/B07D28QKHY?s=hi)
3 | GPS Breakout | Elmwoods | 1 | $52.99 | $0.00 | $52.99 | https://elmwoodelectronics.ca/products/adafruit-ultimate-gps-breakout-66-channel-w-10-hz-updates-version-3
4 | NXP IMU | Elmwoods | 1 | $19.99 | $0.00 | $19.99 | https://elmwoodelectronics.ca/products/adafruit-precision-nxp-9-dof-breakout-board-fxos8700-fxas21002
5 | RPi Camera | Elmwoods | 1 | $39.99 | $0.00 | $39.99 | Raspberry Pi NoIR Camera Board v2- 8MP Infrared-sensitive Camera - Elmwood Electronics (https://elmwoodelectronics.ca/products/raspberry-pi-noir-camera-board-infrared-sensitive-camera) | Out of stock
6 | RPi Camera Cable | Elmwoods | 1 | $4.99 | $0.00 | $4.99 | https://elmwoodelectronics.ca/products/flex-cable-for-raspberry-pi-camera-24-610mm
7 | Pi Cobbler Breakout | Elmwoods | 1 | $11.99 | $0.00 | $11.99 | https://elmwoodelectronics.ca/products/assembled-pi-t-cobbler-plus-gpio-breakout-for-raspberry-pi-b
8 | Protohat | Elmwoods | 1 | $7.99 | $0.00 | $7.99 | https://elmwoodelectronics.ca/products/adafruit-perma-proto-hat-for-pi-mini-kit-no-eeprom
9 | GPS Antenna | Elmwoods | 1 | $19.99 | $0.00 | $19.99 | https://elmwoodelectronics.ca/products/gps-antenna-external-active-antenna-3-5v-28db-5-meter-sma
10 | LiPo Battery | Amazon | 1 | $39.99 | $0.00 | $39.99 | https://www.amazon.ca/Tattu-850mAh-Battery-Racing-Quadcopters/dp/B07218SB7L?s=electronics
11 | LiPo Charger | Amazon | 1 | $22.99 | $0.00 | $22.99 | melasta 9.6V 7.2V 8.4V RC Car Battery Charger for Traxxas NiMH 7 Cell Hump 6 Cell Batteries, Vehicles - Amazon Canada (https://www.amazon.ca/dp/B088CXW8CH?s=electronics)
12 | Motor Driver | Elmwoods | 1 | $10.99 | $0.00 | $10.99 | https://elmwoodelectronics.ca/products/adafruit-drv8871-dc-motor-driver-breakout-board-3-6a-max | Out of stock
13 | White Cane | Amazon | 1 | $21.99 | $0.00 | $21.99 | https://www.amazon.ca/Baitaihem-Folding-Reflective-Walking-Impaired/dp/B07CNM85NV
14 | Ear Buds | Amazon | 1 | $49.89 | $0.00 | $49.89 | https://www.amazon.ca/KORSKR-Bluetooth-Earphones-Waterproof-Microphone/dp/B0B2QZCWNQ?s=electronics
15 | Aluminum mounting hub | Amazon | 1 | $12.49 | $0.00 | $12.49 | https://www.amazon.ca/uxcell%C2%AE-Flange-Coupling-Coupler-Connector/dp/B07PDZD2Y6
17 | Omniwheel | Amazon | 1 | $75.14 | $0.00 | $75.14 | https://www.amazon.ca/Accessories-Aluminum-Double-Competition-Omni-Directional/dp/B07TJYQBSJ
18 | 4mmx100mm shaft (18pcs for sale) | Amazon | 2 | $1.00 | $0.00 | $2.00 | https://www.amazon.ca/Glarks-Stainless-Assorted-Diameter-2-5-8mm/dp/B07CLMCD7N
 |  |  |  |  | TOTAL: | $550.43

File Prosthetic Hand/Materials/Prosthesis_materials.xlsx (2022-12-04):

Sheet: Prototype building
Product | Units | Market | Link |  | Arrived
ADAFRUIT DRV8833 DC/STEPPER MOTO | 2 | Digi-Key | https://www.digikey.ca/en/products/detail/adafruit-industries-llc/3297/6419360 | For micro metal DC motor | x
3pcs 2-Way DC Motor Driver Module 1.5A 2V-10V PWM Speed Regulation Dual H-Bridge Replace L298N | 1 | Amazon | https://www.amazon.ca/dp/B087X9KBC7 | For micro metal DC motor | x
DC Motor + Stepper FeatherWing Add-on For All Feather Boards | 3 | Digi-Key | https://www.digikey.ca/en/products/detail/adafruit-industries-llc/3243/10418971 | For disc vibrator motor, not LRA. Will allow control of up to 12 vibrators at same time | x
Adafruit TCA9548A I2C Multiplexer [ADA2717] | 1 | Amazon | https://www.amazon.ca/Adafruit-TCA9548A-I2C-Multiplexer-ADA2717/dp/B017C09ETS
80LB (300 yards) Reaction Tackle Braided Fishing Line | 1 | Amazon | https://www.amazon.ca/Reaction-Tackle-Green-120LB-300yd/dp/B09CW463RH |  | x
50 Pcs Guitar Finger Guards, Finger Protector Covers Caps Silicone | 1 | Amazon | https://www.amazon.ca/Protector-Silicone-Protectors-Fingertip-Acoustic/dp/B08P5B6CB3 |  | x
Arduino nano | 1 | Amazon | https://www.amazon.ca/KEYESTUDIO-Atmega328P-Arduino-Similar-Breadboard-friendly/dp/B01FSDVZ98 |  | x
Arduino nano 33 BLE | 1 | Canadarobotix | https://www.canadarobotix.com/products/2493
Micro USB to Type 2 Micro B Male | 1 | Amazon | https://www.amazon.ca/dp/B003XRI1UI?s=pc |  | x
1000:1 Micro Metal Gearmotor HP 6V with Extended Motor Shaft | 3 | Pololu | https://www.pololu.com/product/2373 |  | x
380:1 Micro Metal Gearmotor HP 6V with Extended Motor Shaft | 3 | Pololu | https://www.pololu.com/product/4795 |  | x
6V, 5.5A Step-Down Voltage Regulator D36V50F6 | 1 | Pololu | https://www.pololu.com/product/4092 |  | x
Pololu Adjustable Step-Up/Step-Down Voltage Regulator S7V8A 500 mA to 1 A | 1 | Pololu | https://www.pololu.com/product/2118 |  | x
Pololu 3.3V Step-Up/Step-Down Voltage Regulator S7V8F3 | 1 | Pololu | https://www.pololu.com/product/2122 |  | x
5V, 1A Step-Up/Step-Down Voltage Regulator S13V10F5 | 1 | Pololu | https://www.pololu.com/product/4083 |  | x
Magnetic Encoder Pair Kit with Top-Entry Connector for Micro Metal Gearmotors, 12 CPR, 2.7-18V | 3 | Pololu | https://www.pololu.com/product/4760 |  | x
6-Pin Female-Female JST SH-Style Cable 10cm | 3 | Pololu | https://www.pololu.com/product/4765 |  | x
6-Pin Female-Female JST SH-Style Cable 16cm | 6 | Pololu | https://www.pololu.com/product/4766 |  | x
Breakout for JST SH-Style Connector, 6-Pin Male Top-Entry (3-Pack, Untested) | 2 | Pololu | https://www.pololu.com/product/4771 |  | x
BM06B-SRSS-TBT(LF)(SN) | 6 | Digi-Key | https://www.digikey.ca/en/products/detail/jst-sales-america-inc/BM06B-SRSS-TBT-LF-SN/1785724 |  | x
Kit with myoelectric sensors MYO-kit v1.1 | 4 | ELEMYO | https://www.elemyo.com/products/myo_kit1_1
Hosim 2 PCS 7.4V 2000mAh RC Car Rechargeable Li-Po Battery Pack with 1 PCS 2AUSB, 1 PCS Battery Bag and 1PCS Battery Strap for Hosim 1:10 Scale 9125 High Speed Remote Control RC Truck Spare Replacement Parts Accessory Supplies SDL-103562 | 1 | Amazon | https://www.amazon.ca/Hosim-2000mAh-Rechargeable-Li-Po-Battery/dp/B08FD81F4F | Battery for the motors | x
DC 3.7V 1600mAh 103048 li-ion Lithium Ion Polymer Battery Replacement for DIY 3.7-5V Electronic Product, Mobile Energy Storage Power Supply | 2 | Amazon | https://www.amazon.ca/3000mAh-103665-Lithium-Replacement-Bluetooth/dp/B091XYZ2V3 | Battery for MCUs and vibrators | x
Adafruit Micro Lipo w/MicroUSB Jack - USB LiIon/LiPoly charger - v1 [ADA1904] | 1 | Amazon | https://www.amazon.ca/Adafruit-Micro-Lipo-MicroUSB-Jack/dp/B00MJ0HOKS
JST-PH JST Connector Kit, 2.0mm Pitch Female Pin Header, JST PH - 2/3/4/5/6/7 Pin Housing Adapter Cable Connector Socket Male and Female with 2.0mm Female Pin Header Connector, Crimp DIP Kit-1170PCS | 1 | Amazon | https://www.amazon.ca/JST-PH-Connector-2-0mm-Female-Header/dp/B08JCRH8J7 |  | x
Twidec/10Pcs AC 6A/250V 10A/125V SPST 2 Pins 2 Position ON/Off Car Boat Square Black Rocker Switch Toggle with Pre-soldered Wires（Quality Assurance for 1 Years） KCD1-3-101-X | 1 | Amazon | https://www.amazon.ca/Twidec-Pre-soldered-Wires%EF%BC%88Quality-Assurance-KCD1-3-101-X/dp/B07SPY9H7Y |  | x
TUOFENG 30 Gauge Electrical Wire, Colored Wire Kit 30 AWG Flexible Silicone Wire(6 Different Colored 66 Feet spools) 60V Electronics Wire | 1 | Amazon | https://www.amazon.ca/TUOFENG-Wire-Solid-Different-Colored-spools/dp/B07GBYPHBC?s=industrial |  | x
26 Gauge 2 Conductor Electrical Wire 26 AWG Electrical Wire Stranded PVC Cord Pure Copper Cable 10 M / 32.8FT Flexible Low Voltage LED Cable for LED Strips Lamps Lighting Automotive(26/2 AWG-10M) | 1 | Amazon | https://www.amazon.ca/Conductor-Electrical-Stranded-Flexible-Automotive/dp/B093LCQQFY?s=industrial |  | x
eSUN Flexible TPU Filament 1.75mm, 3D Printer Filament TPU-95A, Dimensional Accuracy +/- 0.05mm, 1KG (2.2 LBS) Spool 3D Printing Filament for 3D Printers, Gray | 1 | Amazon | https://www.amazon.ca/eSUN-Flexible-Filament-Dimensional-Accuracy/dp/B091CMXSTH |  | x
AMZ3D 1.75mm PLA 3D Printer Filament, Black, 1 Kg spool (2.2 lbs) | 1 | Amazon | https://www.amazon.ca/AMZ3D-1-75mm-Printer-Filament-Black/dp/B01BZ5ND8O?rnid=11192166011 |  | x
650pcs Heat Shrink Tubing Black innhom Heat Shrink Tube Wire Shrink Wrap UL Approved Ratio 2:1 Electrical Cable Wire Kit Set Long Lasting Insulation Protection, Safe and Easy, Eco-Friendly Material | 1 | Amazon | https://www.amazon.ca/650pcs-Shrink-Tubing-innhom-Approved/dp/B07WWWPR2X |  | x
Rngeo 2 Pack 3/8'' Heat Shrink Tube 3:1 Adhesive-Lined Heat Shrinkable Tubing Black & Red 4Ft | 1 | Amazon | https://www.amazon.ca/Rngeo-Pack-Heat-Shrink-Tube/dp/B0892GTRRL |  | x
PICOBLADE 7 CIRCUIT 300MM | 2 | Digi-Key | https://www.digikey.ca/en/products/detail/molex/0151340703/6198161 |  | x
CONN HEADER VERT 7POS 1.25MM | 4 | Digi-Key | https://www.digikey.ca/en/products/detail/molex/0530470710/242858 |  | x
Brekmis 900 PCS Heat Shrink Tubing 2:1 Shrink Wrap Tube 5 Colors 12 Sizes Wire Cable Wrap Assortment Electric Insulation Shrink Tube Kit with Storage Case | 1 | Amazon | https://www.amazon.ca/Brekmis-900-Heat-Shrink-Tubing/dp/B092342SZK?s=industrial |  | x
5PCS 10x2mm Micro DC Vibrating Motor, DC 3V 80mA 11000±2500rpm Flat Coin Button-Type Mini Vibration Motor for Smart Cell Phone Pager Tablet(27mm) | 1 | Amazon | https://www.amazon.ca/dp/B089NTLLWB/?coliid=I3SHLB6QTZHJKF&colid=19ZIG9ZNK2RJU |  | x
SWITCH ROCKER DPST 16A 125V | 1 | Digi-Key | https://www.digikey.ca/en/products/detail/e-switch/RA812C1121/3778076
Smooth-On SIL-poxy Rubber Silicone Adhesive - 0.5 oz Tube Silpoxy | 1 | Amazon | https://www.amazon.ca/Smooth-SIL-poxy-Rubber-Silicone-Adhesive/dp/B00NGZHGFI
Cmple - Micro USB Cable Android, USB to Micro USB Cable, High Speed USB 2.0 A Male to Micro B Male, Gold-Plated USB Charging Cable for Samsung, HTC, Tablet and More - 6 Feet Black | 1 | Amazon | https://www.amazon.ca/dp/B003XRI6L2?s=pc
RGBZONE 120pcs Multicolored Dupont Wire 40pin Male to Female, 40pin Male to Male, 40pin Female to Female Breadboard Jumper Wires Ribbon Cables Kit for Arduino and Raspberry Pi | 1 | Amazon | https://www.amazon.ca/RGBZONE-Multicolored-Breadboard-Arduino-Raspberry/dp/B08TWSV2DY?s=electronics
Multimeter | 1 | Amazon | https://www.amazon.ca/ProTechTrader-PDM-711-Screen-Digital-Multimeter/dp/B07FN91625
Adafruit 259, USB Li-Ion/LiPoly Charger, v1.2 | 1 | Amazon | https://www.amazon.ca/Adafruit-259-Li-Ion-LiPoly-Charger/dp/B00E4WLX1K
INCREWAY 1050pcs Metric M1.4 M1.6 M2 M2.5 Laptop Notebook Computer Screw Assortment Kit for IBM HP Dell Lenovo Samsung Sony Toshiba Gateway Hacer | 1 | Amazon | https://www.amazon.ca/INCREWAY-1050pcs-Notebook-Computer-Assortment/dp/B07KN4C9XV | * Need the M1.6*5mm screws
160pcs M2 M2.5 M3 M4 M5 304 Stainless Steel Pan Head Screws Nuts Assortment Kit with Storage Box | 1 | Amazon | https://www.amazon.ca/160pcs-Stainless-Screws-Assortment-Storage/dp/B074FH9SXQ | *Need the M2.5*8mm screws

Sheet: prev_materials
Product | Units | Market | Link
5PCS 10x2mm Micro DC Vibrating Motor, DC 3V 80mA 11000±2500rpm Flat Coin Button-Type Mini Vibration Motor for Smart Cell Phone Pager Tablet(27mm) | 2 | Amazon | https://www.amazon.ca/dp/B089NTLLWB/?coliid=I3SHLB6QTZHJKF&colid=19ZIG9ZNK2RJU
2Pcs Thin Film Pressure Sensor, High Precise Force-Sensitive Resistor Force Sensor Pressure Sensor Resistance-Type Thin Film Pressure Sensor, Force Sensing Resistor | 1 | Amazon | https://www.amazon.ca/dp/B07T1CHY58/?coliid=I2BXVPN0XJKUDV&colid=19ZIG9ZNK2RJU
LET'S RESIN Silicone Mold Making Kit Liquid Silicone Rubber Non-Toxic Translucent Clear Mold Making Silicone-Mixing Ratio 1:1-Molding Silicone for Resin Molds,Silicone Molds DIY Manual Making(21.16oz) | 1 | Amazon | https://www.amazon.ca/LETS-RESIN-Silicone-Making-Non-Toxic/dp/B07V5FFPWC
Silicone Resin Measuring Cups Tool Kit, Reusable Nonstick Silicone Mat, 100ml Silicone Measuring Cups, Finger Cots, Resin Mix Cup, Stir Stick Pipette (29PCS) | 1 | Amazon | https://www.amazon.ca/dp/B08V515WJF?s=kitchen
Cylewet 6Pcs B2K B5K B10K B20K B50K B100K Ohm Knurled Shaft Linear Rotary Taper Potentiometer with Rotary Knob Cap for Arduino (Pack of 6) CLT1066 | 1 | Amazon | https://www.amazon.ca/Cylewet-Knurled-Potentiometer-Arduino-CLT1066/dp/B07DFHXCZZ?dd=c04fGJKjKTLM_GOB3i0bXQ%2C%2C&rnid=11828086011
10V 200Pcs Diodes Box Set, 1N4001~1N5819 Zener Diode Combination Electronic Kit, Germanium Diode Kit with Transparent Box | 1 | Amazon | https://www.amazon.ca/Regulator-Assortment-Electronic-1N4001-1N4007-1N5817-1N5819/dp/B07CJMBMJS?dd=c04fGJKjKTLM_GOB3i0bXQ%2C%2C&rnid=11828086011
TUOFENG 22 awg Solid Wire-Solid Wire Kit-6 Different Colored 30 Feet/9M spools 22 Gauge Jumper Wire- Hook up Wire Kit | 1 | Amazon | https://www.amazon.ca/TUOFENG-Wire-Solid-Different-Colored-spools/dp/B086WF1WD1
Hilitchi Professional Pin Crimping Tool 2.54mm 3.96mm 28-18awg 0.1-1.0mm² for Dupont Terminals with Wire-Electrode Cutting Die Insulated Terminal Crimper/Stripper/Cutter Tool | 1 | Amazon | https://www.amazon.ca/Hilitchi-Professional-0-1-1-0mm%C2%B2-Terminals-Wire-electrode/dp/B016B39EPQ
Hilitchi 635 Pcs 40 Pin 2.54mm Pitch Single Row Pin Headers, Connector Housing Female, Male/Female Pin Kit for Dupont Wire Connectors | 1 | Amazon | https://www.amazon.ca/Hilitchi-2-54mm-Headers-Connector-Housing/dp/B014YTPFT8?s=industrial
Bessey GSCC2.518 2.5-Inch x 18-Inch Economy Clutch Style Bar Clamp | 1 | Amazon | https://www.amazon.ca/Bessey-GSCC2-518-2-5-Inch-18-Inch-Economy/dp/B000FA2FM6
Winter Thermal Gloves Men Women Touch Screen Anti Slip Water Resistant Windproof in Cold Weather for Driving Cycling Running | 1 | Amazon | https://www.amazon.ca/OZERO-Cycling-Driving-Sensitive-Texting/dp/B07S92X3RM?asc_contenttype=article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
Leyeet Black Arm Band, 15 Pcs Elastic Adjustable Armband Sports Team Football Soccer Respect Funeral Mourning Armband for Men and Women | 1 | Amazon | https://www.amazon.ca/Elastic-Armband-Respect-Mourning-Football/dp/B07L5LS6DD
Etekcity Food Kitchen Scale, Digital Grams and Ounces for Weight Loss, Baking, Cooking, Keto and Meal Prep, Small, 304 Stainless Steel | 1 | Amazon | https://www.amazon.ca/Etekcity-Multifunction-Stainless-Batteries-Included/dp/B0113UZJE2
Interlink Electronics Series FSR™400 | 5 | Digi-key | https://www.digikey.ca/en/products/detail/interlink-electronics/34-00004/2798665
Smooth-On SIL-poxy Rubber Silicone Adhesive - 0.5 oz Tube Silpoxy | 1 | Amazon | https://www.amazon.ca/Smooth-SIL-poxy-Rubber-Silicone-Adhesive/dp/B00NGZHGFI

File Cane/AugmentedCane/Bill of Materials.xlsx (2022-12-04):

Number | Part Name | Vendor | Quantity | Cost | Shipping | Total Cost | Link
1 | Raspberry Pi 4b+ (4 GB) | Adafruit | 1 | $55.00 | $0.00 | $55.00 | https://www.adafruit.com/product/4296
2 | RPLidar A1 | Amazon | 1 | $99.99 | $0.00 | $99.99 | https://www.amazon.com/Slamtec-RPLIDAR-Scanning-Avoidance-Navigation/dp/B07TJW5SXF?hvadid=385584089652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
3 | Motor | Pololu | 1 | $19.95 | $0.00 | $19.95 | https://www.pololu.com/product/3225
4 | GPS Breakout | Adafruit | 1 | $39.95 | $0.00 | $39.95 | https://www.adafruit.com/product/746
5 | NXP IMU | Adafruit | 1 | $14.95 | $0.00 | $14.95 | https://www.adafruit.com/product/3463
6 | RPi Camera | Adafruit | 1 | $29.95 | $0.00 | $29.95 | https://www.adafruit.com/product/3099
7 | RPi Camera Cable | Adafruit | 1 | $2.95 | $0.00 | $2.95 | https://www.adafruit.com/product/1731
8 | Pi Cobbler Breakout | Adafruit | 1 | $6.95 | $0.00 | $6.95 | https://www.adafruit.com/product/1754
9 | Protohat | Adafruit | 1 | $4.95 | $0.00 | $4.95 | https://www.adafruit.com/product/2310
10 | GPS Antenna | Adafruit | 1 | $14.95 | $0.00 | $14.95 | https://www.adafruit.com/product/960
11 | Micro SD Card | Amazon | 1 | $6.90 | $0.00 | $6.90 | https://www.amazon.com/Sandisk-Ultra-Micro-UHS-I-Adapter/dp/B073K14CVB?cv_ct_cx=16gb+sd&s=electronics
12 | LiPo Battery | Amazon | 1 | $13.00 | $0.00 | $13.00 | https://www.amazon.com/dp/B072PPRPRN
13 | LiPo Charger | Amazon | 1 | $12.00 | $0.00 | $12.00 | https://www.amazon.com/Blomiky-Charger-11-1V-Balance-Battery/dp/B072K5LHGM?s=toys-and-games
14 | USB cable | Adafruit | 1 | $2.95 | $0.00 | $2.95 | https://www.adafruit.com/product/4472
15 | Rechargeable Battery | Amazon | 1 | $12.50 | $0.00 | $12.50 | https://www.amazon.com/gp/product/B07MS1B8KQ/ref=ppx_yo_dt_b_asin_title_o07_s00?ie=UTF8&psc=1
17 | Motor Driver | Adafruit | 1 | $7.50 | $0.00 | $7.50 | https://www.adafruit.com/product/3190
18 | Pi Case | Amazon | 1 | $18.99 | $0.00 | $18.99 | https://www.amazon.com/Miuzei-Raspberry-HDMI-Micro-Aluminum-Included/dp/B07VX2WDHM
19 | White Cane | Amazon | 1 | $17.00 | $0.00 | $17.00 | https://www.amazon.com/Drive-Medical-Deluxe-Folding-Reflective/dp/B002VWK0HI
20 | Ear Buds | Amazon | 1 | $39.99 | $0.00 | $39.99 | https://www.amazon.ca/Ergonomic-Headphones-APEKX-Waterproof-Supporting/dp/B07XFMHQDP?hvadid=80608037718079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
21 | 4mm shaft | Amazon | 1 | $7.99 | $0.00 | $7.99 | https://www.amazon.com/Sutemribor-100mm-Straight-Helicopter-Airplane/dp/B07FYTQWDC
22 | Omniwheel | Robotshop | 1 | $13.50 | $0.00 | $13.50 | https://www.robotshop.com/en/60mm-aluminum-omni-wheel.html
23 | Aluminum mounting hub | Robotshop | 2 | $6.21 | $0.00 | $12.42 | https://www.robotshop.com/en/4mm-aluminum-mounting-hub-60mm-omni-wheel.html
 |  |  |  |  | TOTAL: | $454.33

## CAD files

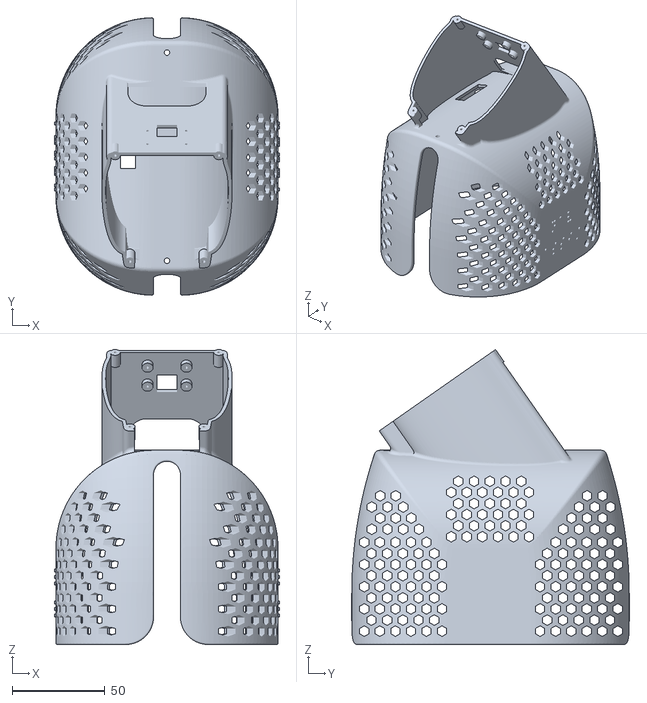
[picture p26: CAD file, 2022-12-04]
Cane/AugmentedCane/cane_hull.stl
121.6 x 150.0 x 159.4

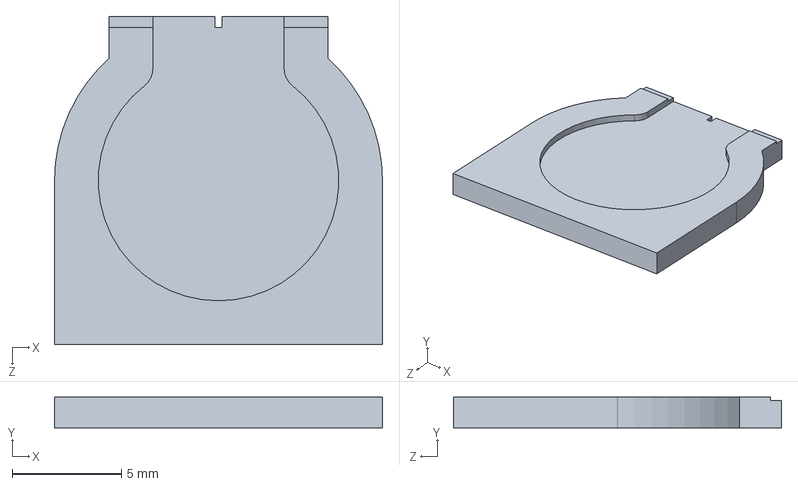
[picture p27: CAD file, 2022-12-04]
Prosthetic Hand/1. CAD/FSR_Layer/FSR_Mold_1.SLDPRT
15.0 x 1.40 x 15.0 mm

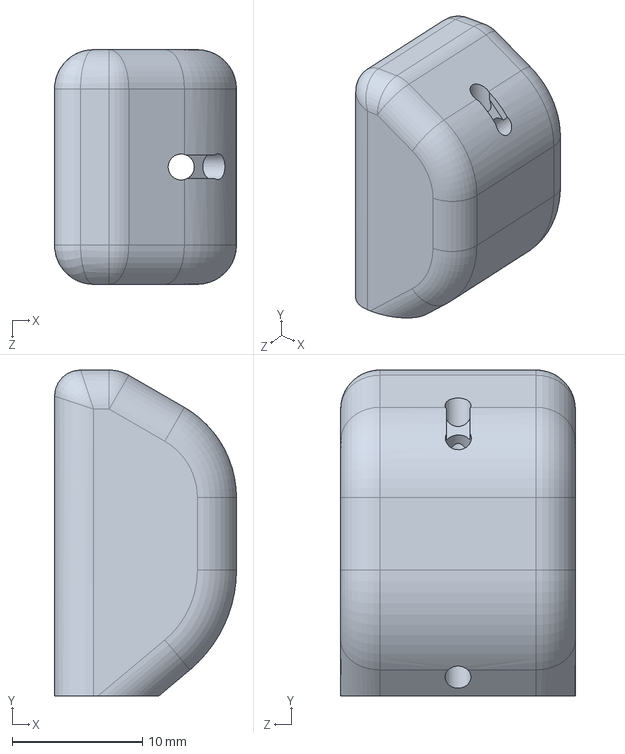
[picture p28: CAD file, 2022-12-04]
Prosthetic Hand/1. CAD/Prosthetic hand/3-3_v2.SLDPRT
14.0 x 25.0 x 18.0 mm

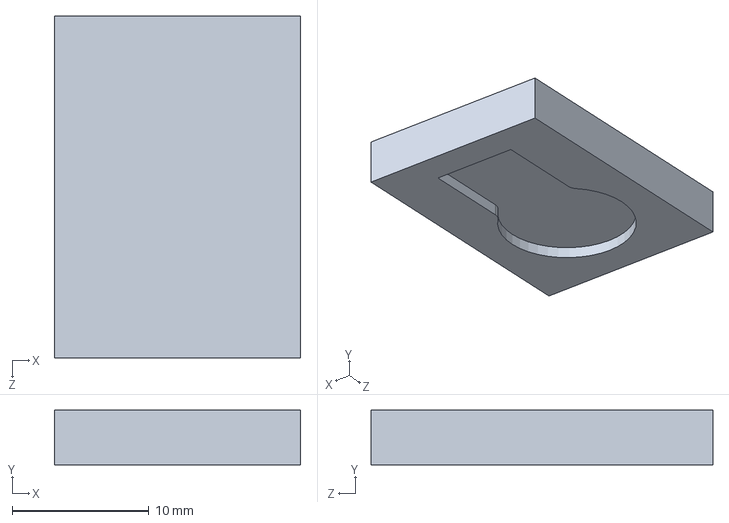
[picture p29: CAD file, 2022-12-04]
Prosthetic Hand/1. CAD/FSR_Layer/FSR_Mold_v2.SLDPRT
18.0 x 4.00 x 25.0 mm

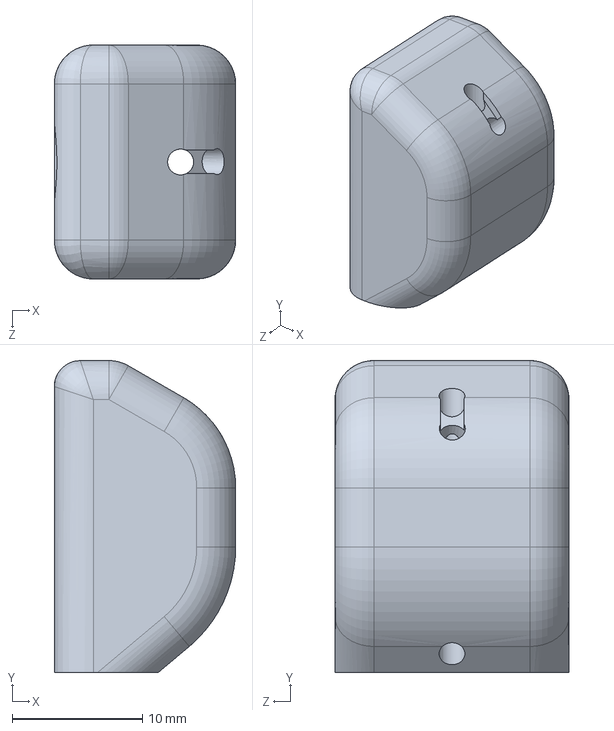
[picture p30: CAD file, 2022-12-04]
Prosthetic Hand/1. CAD/Prosthetic hand/4-3_v2.SLDPRT
14.0 x 24.0 x 18.0 mm

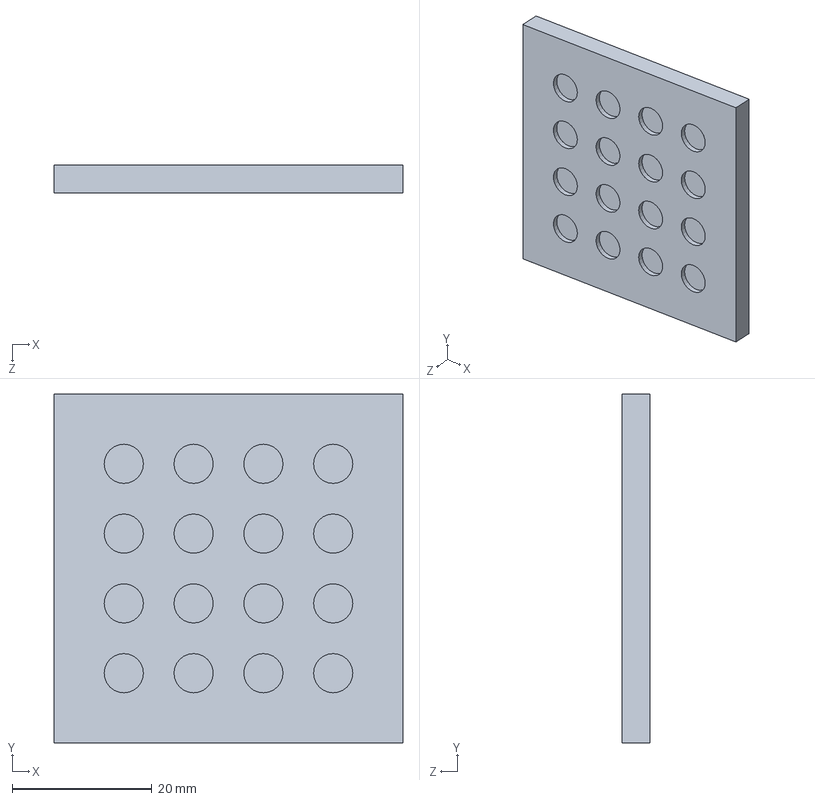
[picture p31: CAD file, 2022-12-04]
Prosthetic Hand/1. CAD/FSR_Layer/FSR_Mold_v3.SLDPRT
50.0 x 50.0 x 4.00 mm

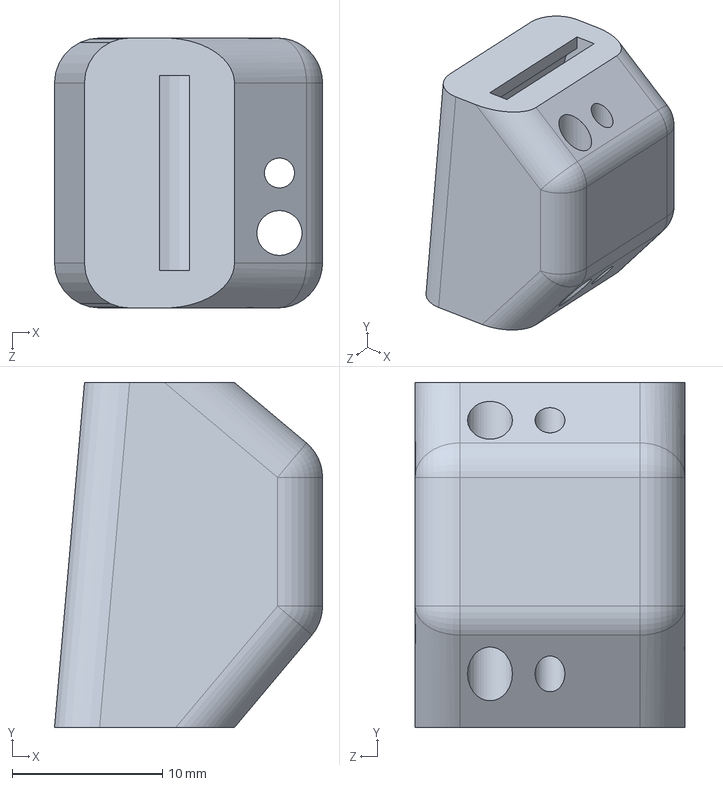
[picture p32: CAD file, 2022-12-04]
Prosthetic Hand/1. CAD/Prosthetic hand/2-2_v2.SLDPRT
17.9 x 23.0 x 18.0 mm

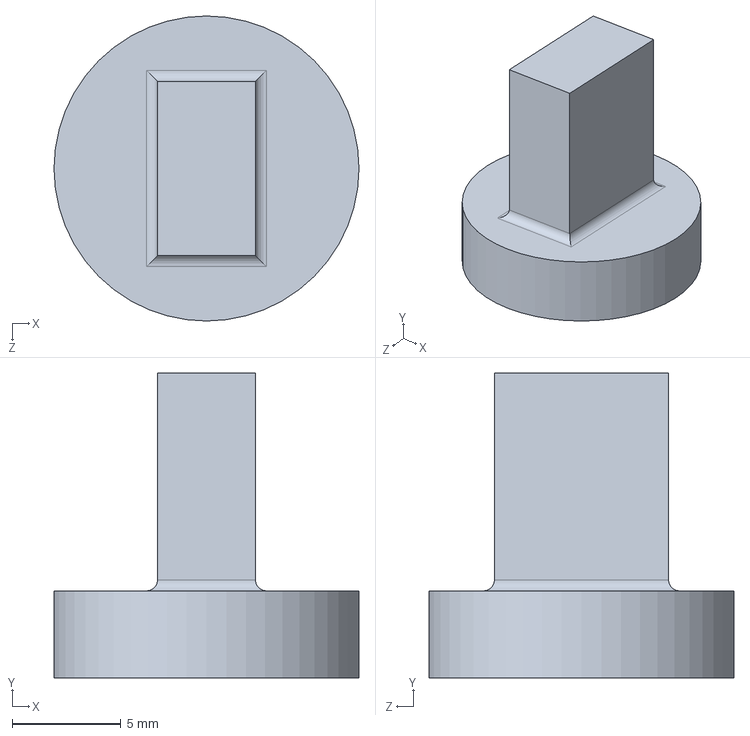
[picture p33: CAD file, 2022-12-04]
Prosthetic Hand/1. CAD/FSR_Layer/Grip_Support_1.SLDPRT
14.0 x 14.0 x 14.0 mm

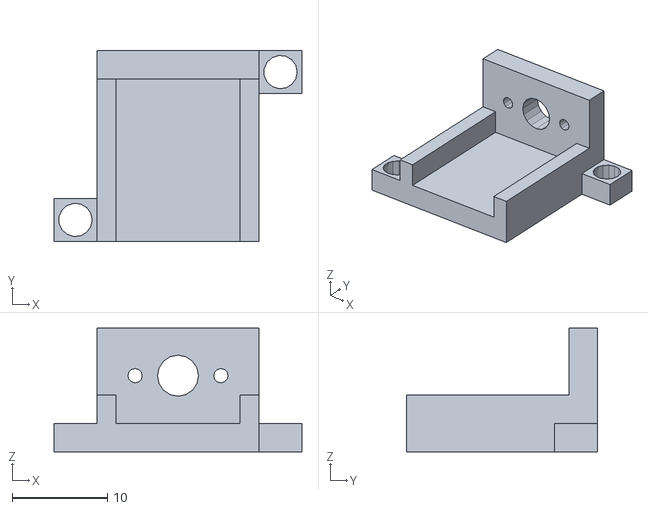
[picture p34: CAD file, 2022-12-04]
Prosthetic Hand/1. CAD/Prosthetic hand/0-3-1.STL
26.0 x 20.0 x 13.0

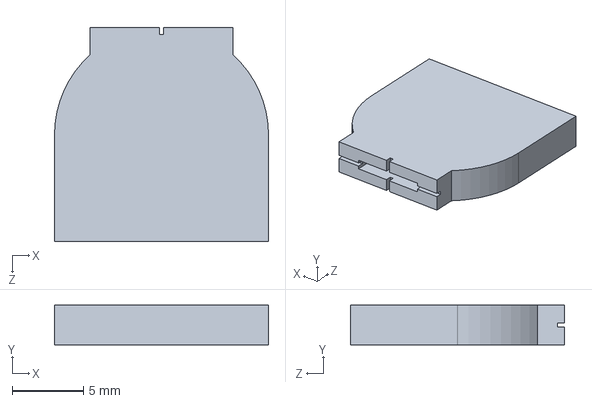
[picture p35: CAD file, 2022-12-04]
Prosthetic Hand/1. CAD/FSR_Layer/FSR_Mold.SLDPRT
15.0 x 2.80 x 15.0 mm

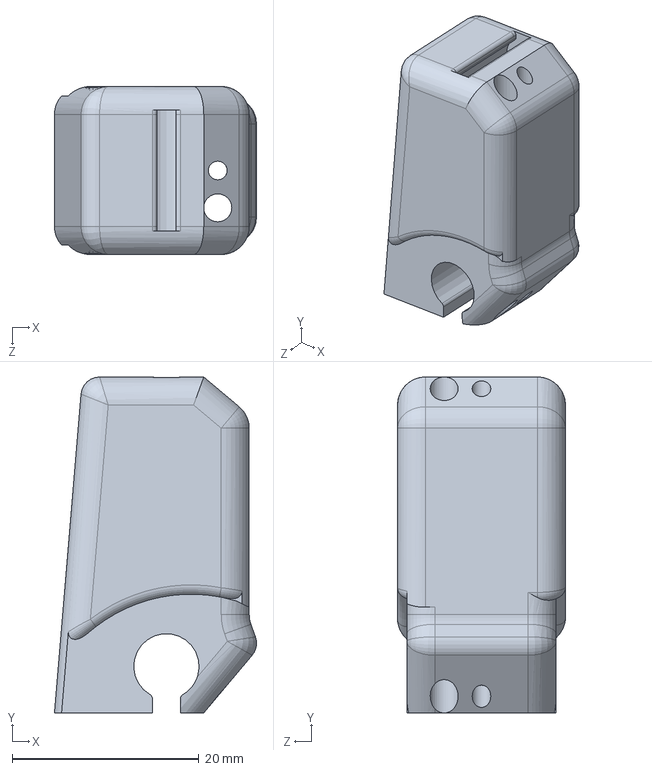
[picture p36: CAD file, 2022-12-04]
Prosthetic Hand/1. CAD/Prosthetic hand/2-1_v2.SLDPRT
21.7 x 36.0 x 18.0 mm

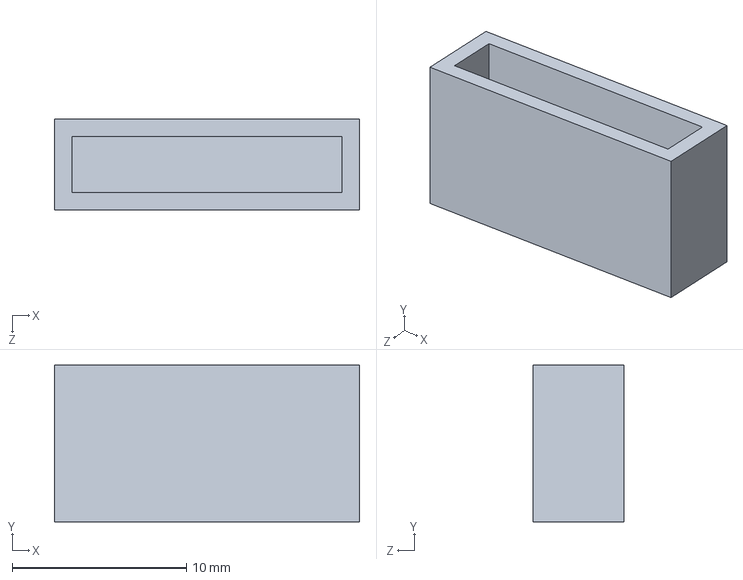
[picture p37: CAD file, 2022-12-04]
Prosthetic Hand/1. CAD/FSR_Layer/FSR_Mold_3.SLDPRT
17.5 x 9.00 x 5.20 mm

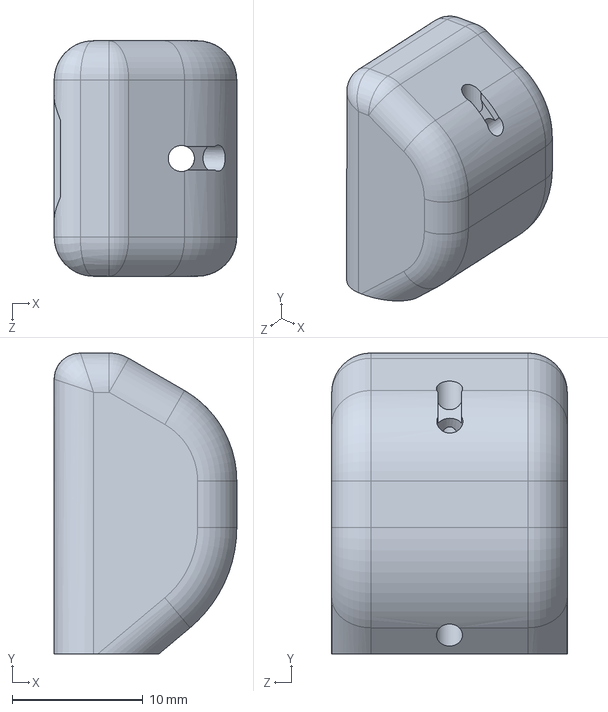
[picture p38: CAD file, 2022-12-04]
Prosthetic Hand/1. CAD/Prosthetic hand/2-3_v2.SLDPRT
14.0 x 23.0 x 18.0 mm

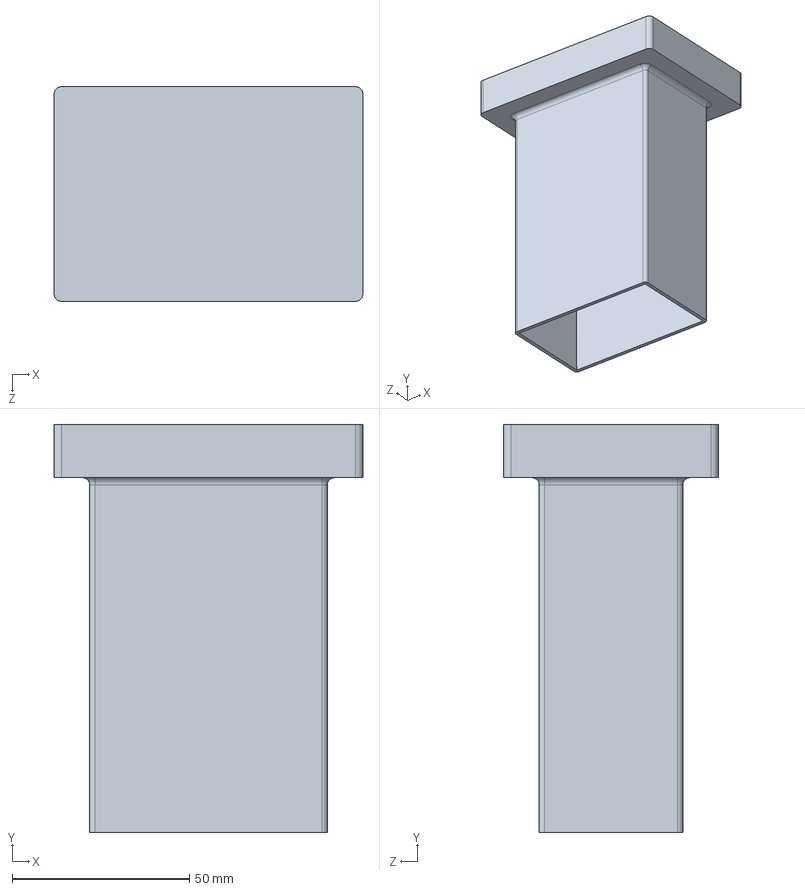
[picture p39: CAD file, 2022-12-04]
Prosthetic Hand/1. CAD/FSR_Layer/Force_Gauge_Support_1.SLDPRT
87.0 x 115.0 x 60.5 mm

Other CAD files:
Prosthetic Hand/1. CAD/Prosthetic hand/6.SLDPRT
Prosthetic Hand/1. CAD/FSR_Layer/FSR_Mold_2.SLDPRT
Prosthetic Hand/1. CAD/Prosthetic hand/4-1_v2.SLDPRT
Prosthetic Hand/1. CAD/Prosthetic hand/0-3-2.SLDPRT
Prosthetic Hand/1. CAD/FSR_Layer/FSR_Mold_1.STL
Prosthetic Hand/1. CAD/FSR_Layer/FSR_Mold_2.STL
Prosthetic Hand/1. CAD/FSR_Layer/FSR_Mold_3.STL
Prosthetic Hand/1. CAD/FSR_Layer/FSR_Mold_v2.STL
Prosthetic Hand/1. CAD/FSR_Layer/FSR_Mold_v3.STL
Prosthetic Hand/1. CAD/FSR_Layer/Force_Gauge_Support_1.STL
Prosthetic Hand/1. CAD/FSR_Layer/Grip_Support_1.STL
Prosthetic Hand/1. CAD/Prosthetic hand/0-1_body_twist_v2.SLDPRT
Prosthetic Hand/1. CAD/Prosthetic hand/0-1_body_twist_v2_1.SLDPRT
Prosthetic Hand/1. CAD/Prosthetic hand/0-1_body_twist_v2_1.STL
Prosthetic Hand/1. CAD/Prosthetic hand/0-3-2.STL
Prosthetic Hand/1. CAD/Prosthetic hand/0-4.SLDPRT
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

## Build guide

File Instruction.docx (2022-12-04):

Motion Sensor Glove

# 1. Hardware:

## 1.1 9DoF Sensor Stick (LSM9DS1)

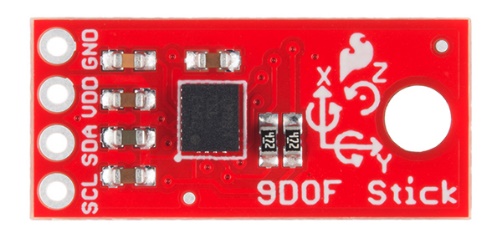
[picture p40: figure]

LSM9DS1 Details:

- 3 acceleration channels, 3 angular rate channels, 3 magnetic field channels
- ±2/±4/±8/±16 g linear acceleration full scale
- ±4/±8/±12/±16 gauss magnetic full scale
- ±245/±500/±2000 dps angular rate full scale
- I2C serial interface
- Operating Voltage: 3.3V

More details:

https://learn.sparkfun.com/tutorials/9dof-sensor-stick-hookup-guide/all

## 1.2 TCA9548A multiplex

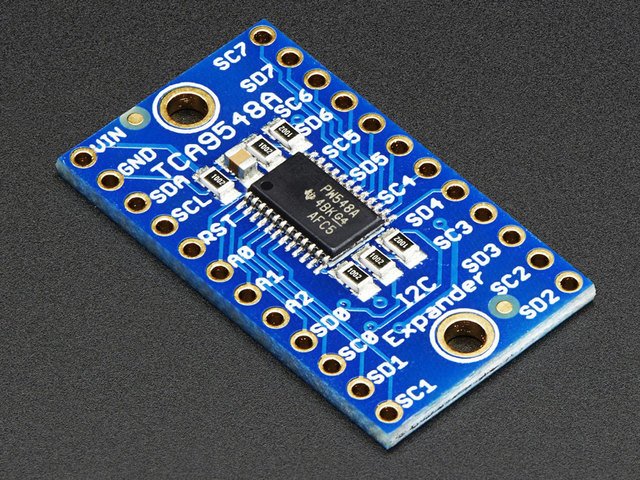
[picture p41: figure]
Adafruit TCA9548A 1-to-8 I2C Multiplexer Breakout

We basically send it a command to tell it which I2C multiplexed output we want to talk to, then we can address the board you want to address.

More details:

https://learn.adafruit.com/adafruit-tca9548a-1-to-8-i2c-multiplexer-breakout

Wiring & Test

Wiring & Test | Adafruit TCA9548A 1-to-8 I2C Multiplexer Breakout | Adafruit Learning System (https://learn.adafruit.com/adafruit-tca9548a-1-to-8-i2c-multiplexer-breakout/wiring-and-test)

## 1.3 Flex Sensor

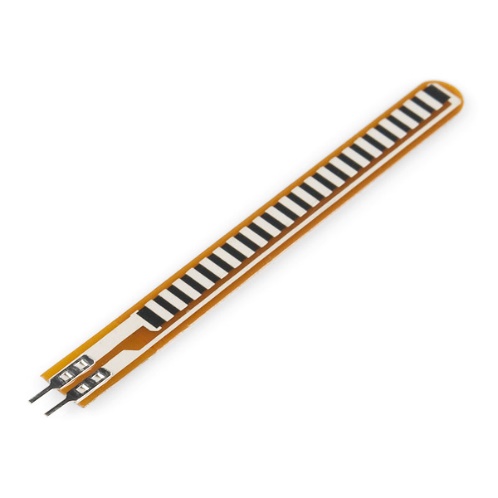
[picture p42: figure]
Flex Sensor 2.2"

The conductive ink printed on the sensor acts as a resistor. When the sensor is straight, this resistance is about 25k. When the sensor is bent, conductive layer is stretched, resulting in reduced cross section (imagine stretching a rubber band). This reduced cross section results in an increased resistance. At 90° angle, this resistance is about 100KΩ. When the sensor is straightened again, the resistance returns to its original value.

More details:

Flex Sensor Features, Working, Circuit & Datasheet (components101.com) (https://components101.com/sensors/flex-sensor-working-circuit-datasheet)

## 1.4 Arduino Uno

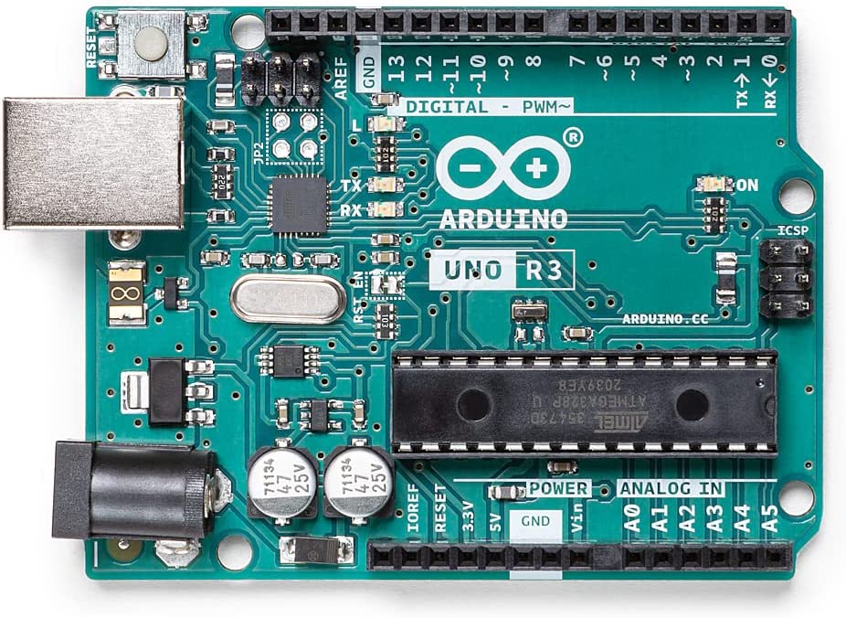
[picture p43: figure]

More Details:

https://store-usa.arduino.cc/products/arduino-uno-rev3

## 1.5 Arduino Mega 2560

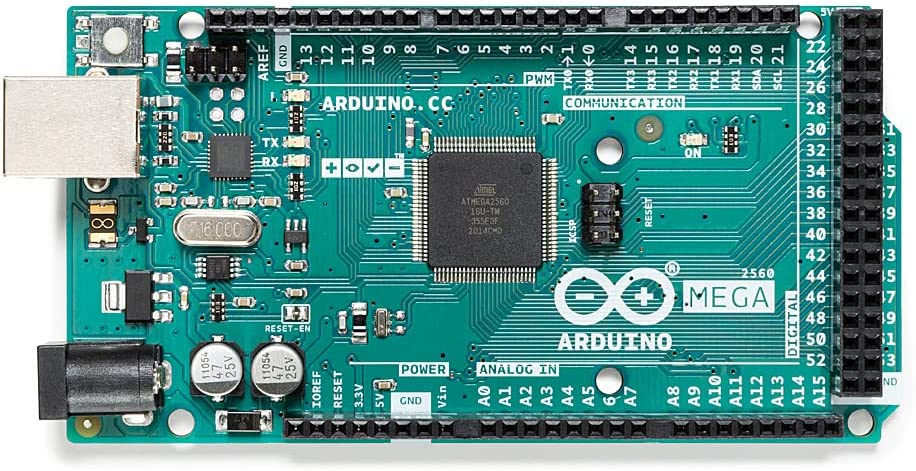
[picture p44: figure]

More details：

https://store-usa.arduino.cc/products/arduino-mega-2560-rev3

# 2. Components:

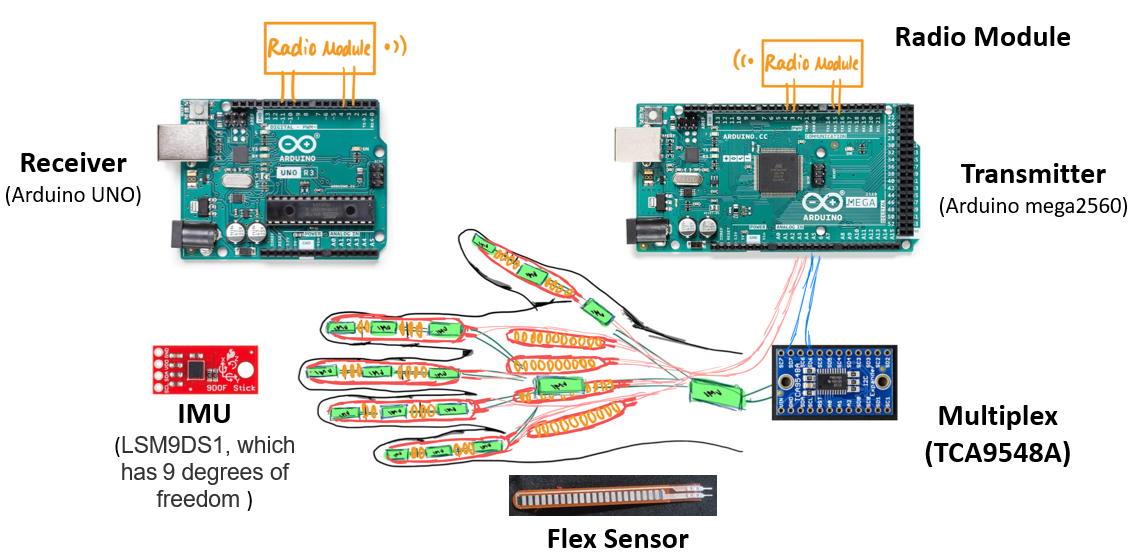
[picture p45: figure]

# 3. Workflow:

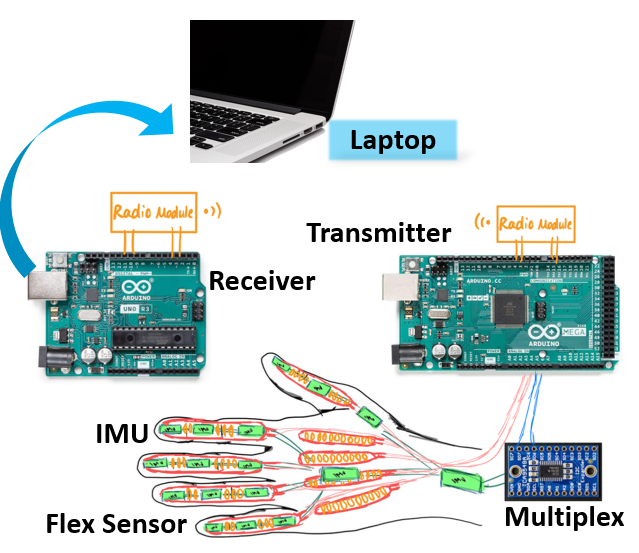
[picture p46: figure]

1. The data from the 16 IMUs and 9 Angle Sensors will be read by the Arduino mega2560.
2. The data read from the sensors will be processed by the Arduino mega2560. Then we can get the acceleration, angular rate, magnetic field, direction data (from IMU) and angle data (from flex sensors)
3. After the Arduino mega2560 get the data, it will work as a transmitter and send the data to the receiver (Arduino Uno), which is connected to the laptop. Then we can see the data from the laptop and do further analysis.

# 4. Instructions for Use:

## 4.1 Add library documents

You need to move the SparkFun_LSM9DS1_Arduino_Library folder and the RadioHead into a libraries folder within your Arduino sketchbook or use the Library Manger to install.

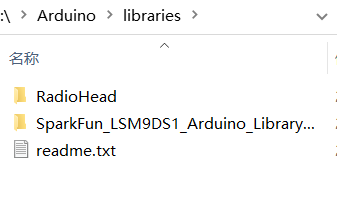
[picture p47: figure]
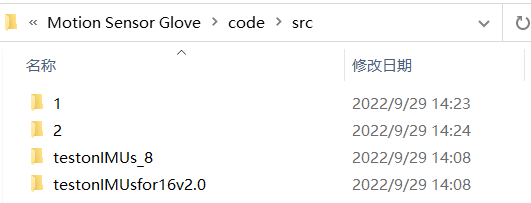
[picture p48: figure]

## 4.2 Upload the code to the Arduino Uno

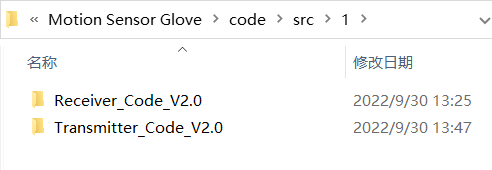
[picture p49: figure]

I wrote two codes to choose from. The code in the first folder which function has been shown in the workflow has two codes. The receiver code should be upload to the Arduino Uno. The transmitter code should be upload to the Arduino Mega2560.

Here is the receiver part:

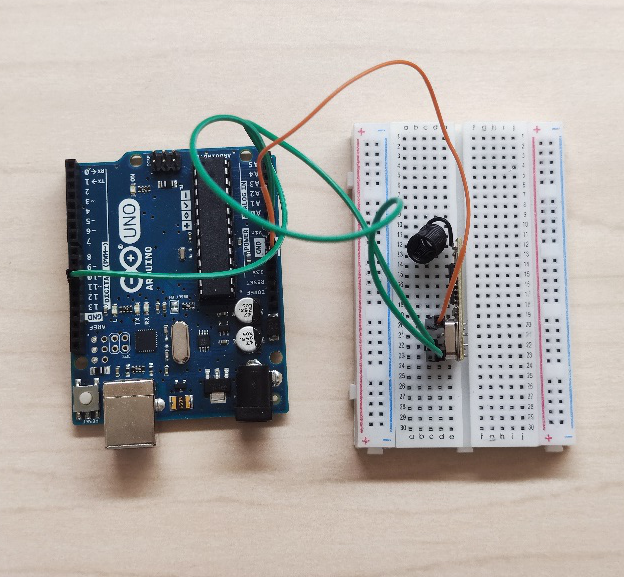
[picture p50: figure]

Choose the board in Arduino IDE and connect the Arduino Uno to your laptop.

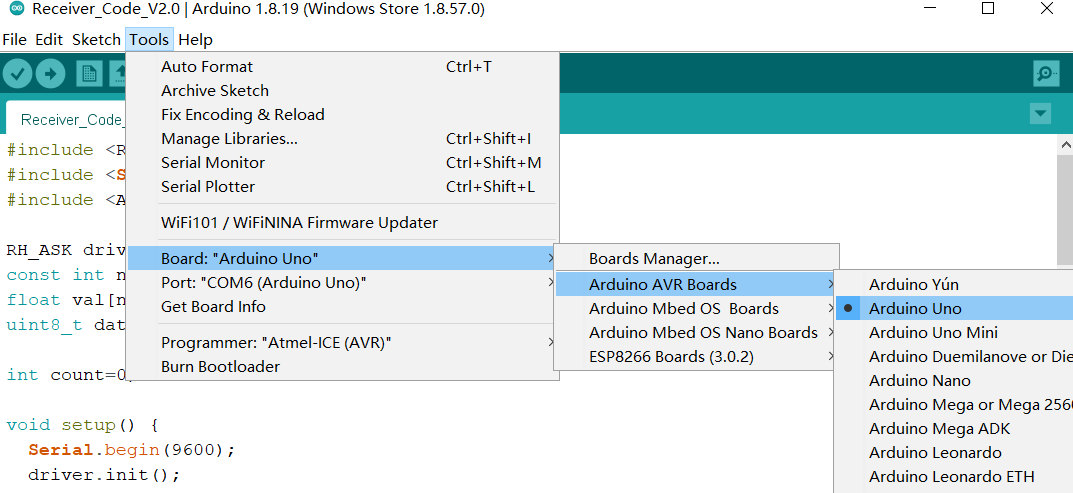
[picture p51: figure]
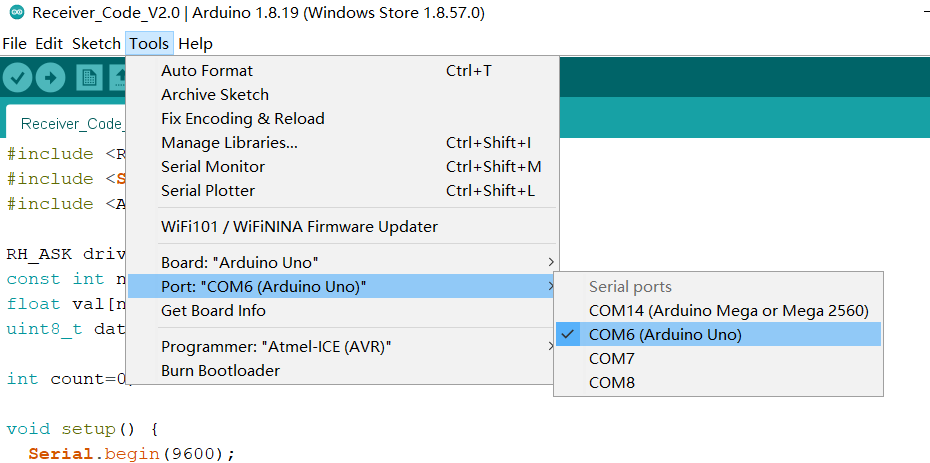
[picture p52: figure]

If you have connected it successfully, you will see this:

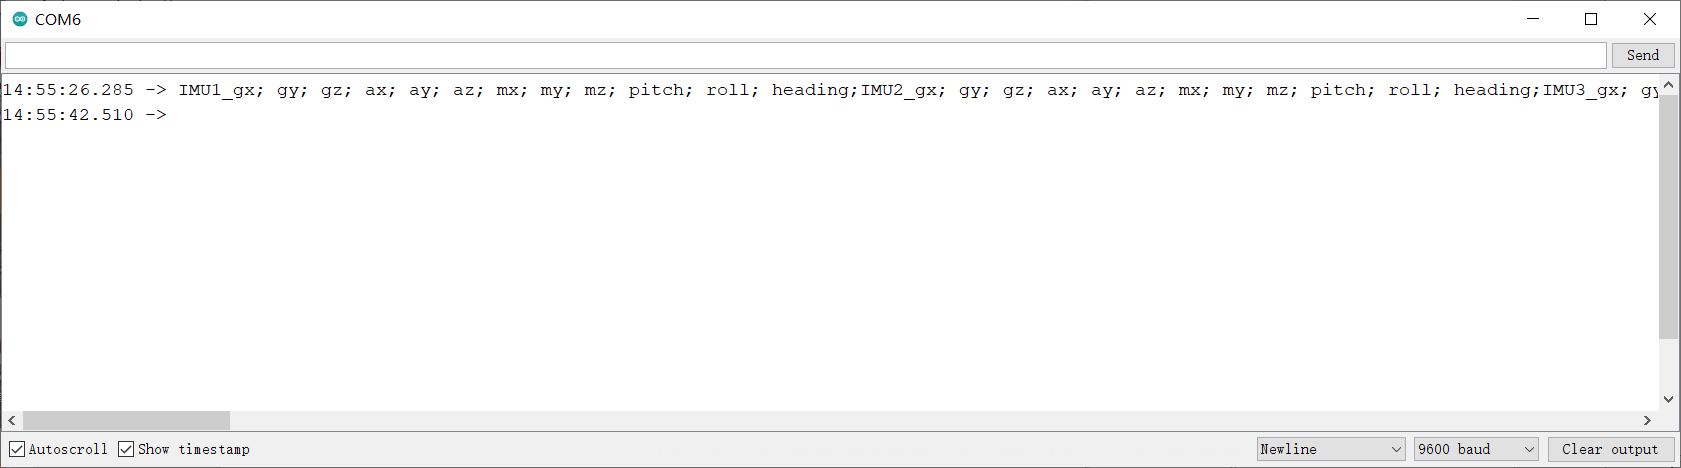
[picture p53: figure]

## 4.3 Upload the code to the Arduino Mega2560

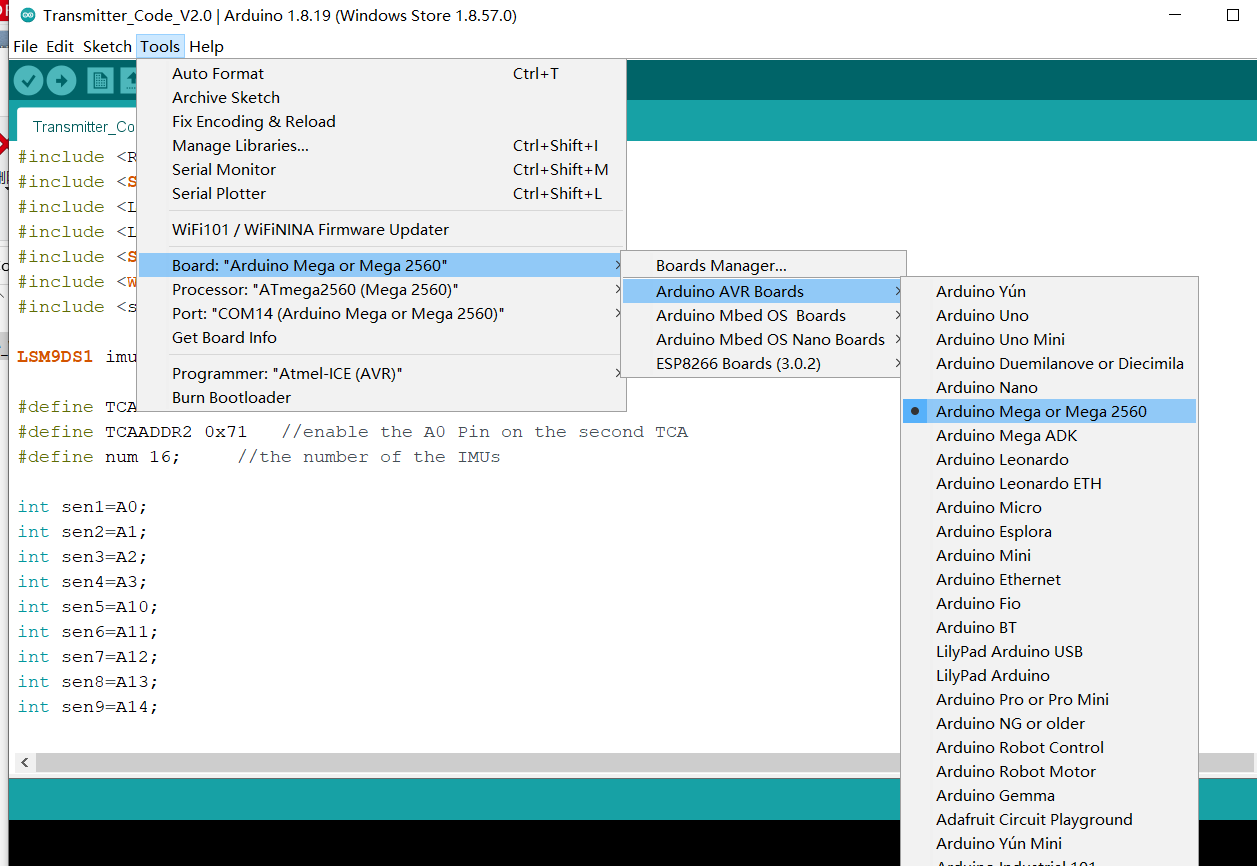
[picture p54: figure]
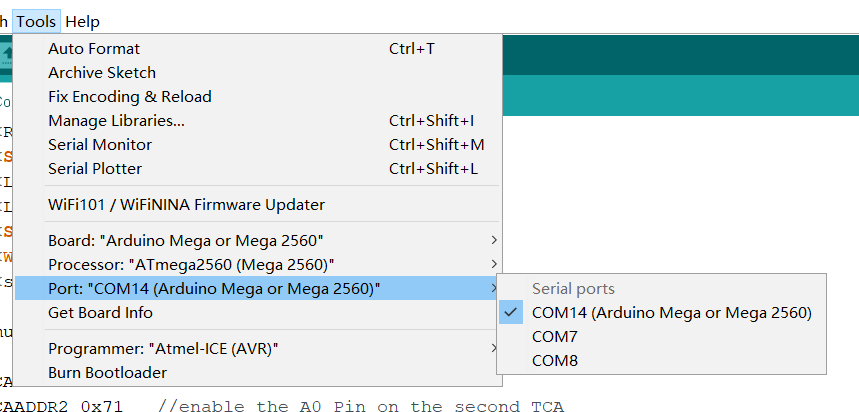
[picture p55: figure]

## 4.4 Open the Serial Monitor

You will see some data sent by the Arduino Mega2560, like the picture below. This means it has initialized successfully.

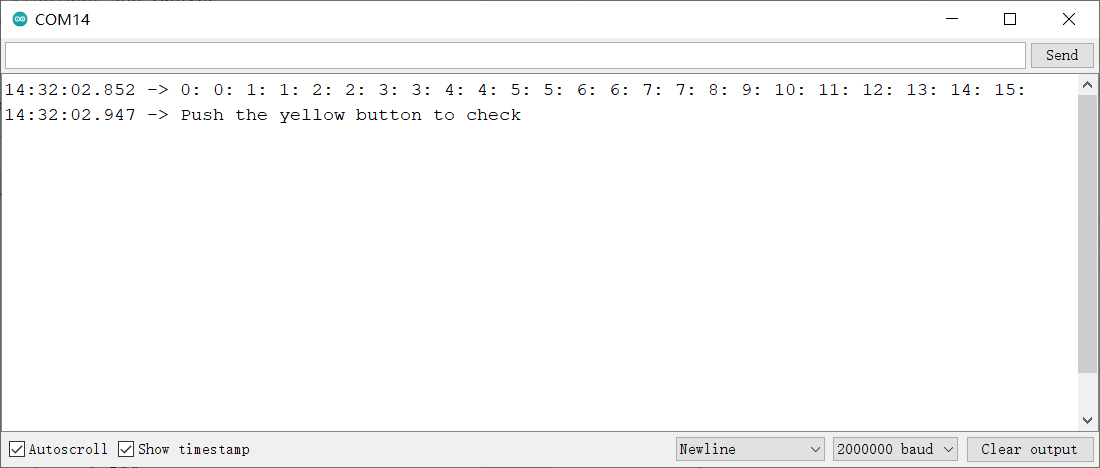
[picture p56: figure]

Remember to set the baud rate according to different code. The baud rate used in the code is showed below:

Code filename | Baud rate
Receiver_Code_V2.0 | 9 600
Transmitter_Code_V2.0 | 115 200
Transmitter_Code_V2.7 | 2 000 000
testonIMUs_8 | 115 200
testonIMUsfor16v2.0 | 115 200

## 4.5 Initialize the Flex sensors

Press once the yellow button

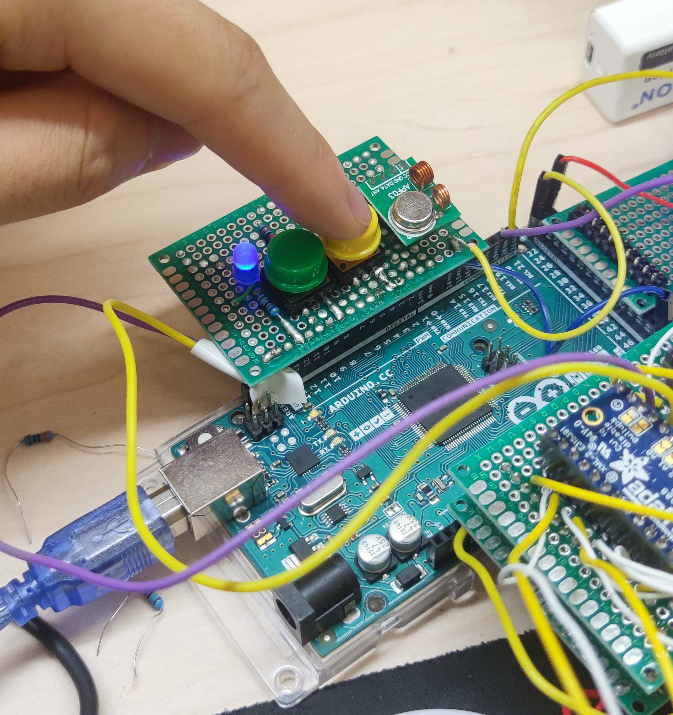
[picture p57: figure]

About 2 seconds later, you will see this

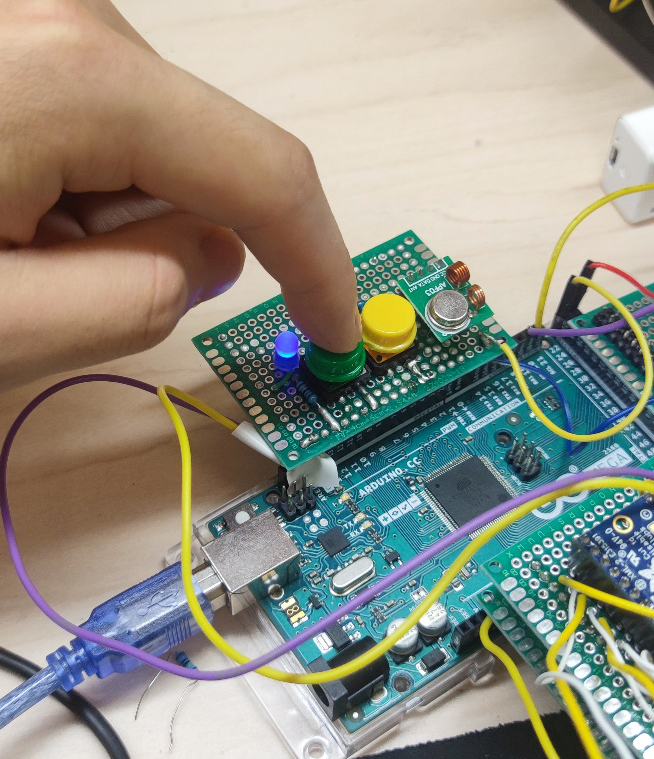
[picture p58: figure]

Then we can begin.

## 4.6 Start

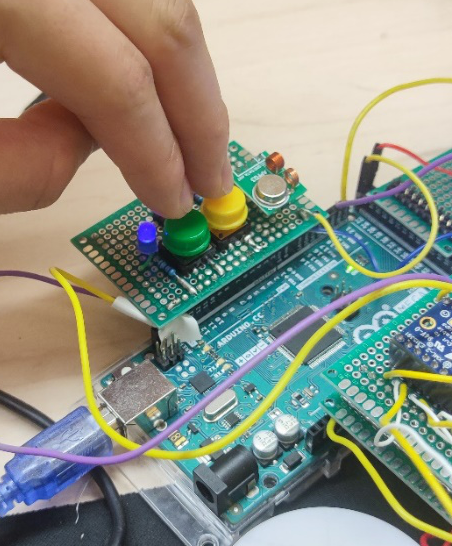
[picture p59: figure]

Mode1

Form the transmitter (Arduino Mega2560) Serial Monitor, you can result see like this:

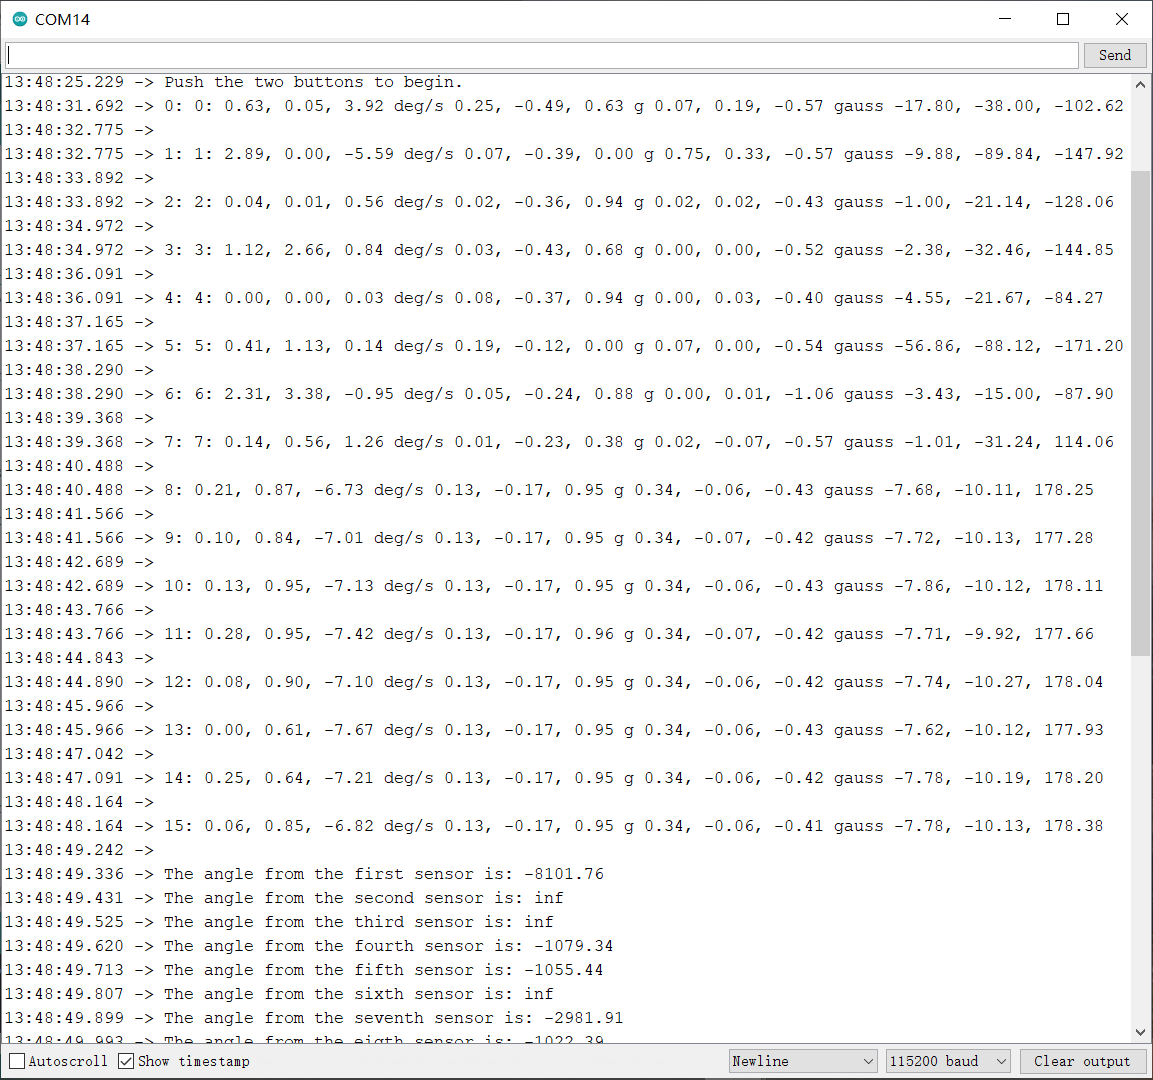
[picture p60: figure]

Form the receiver (Arduino Uno) Serial Monitor, you can result see like this:

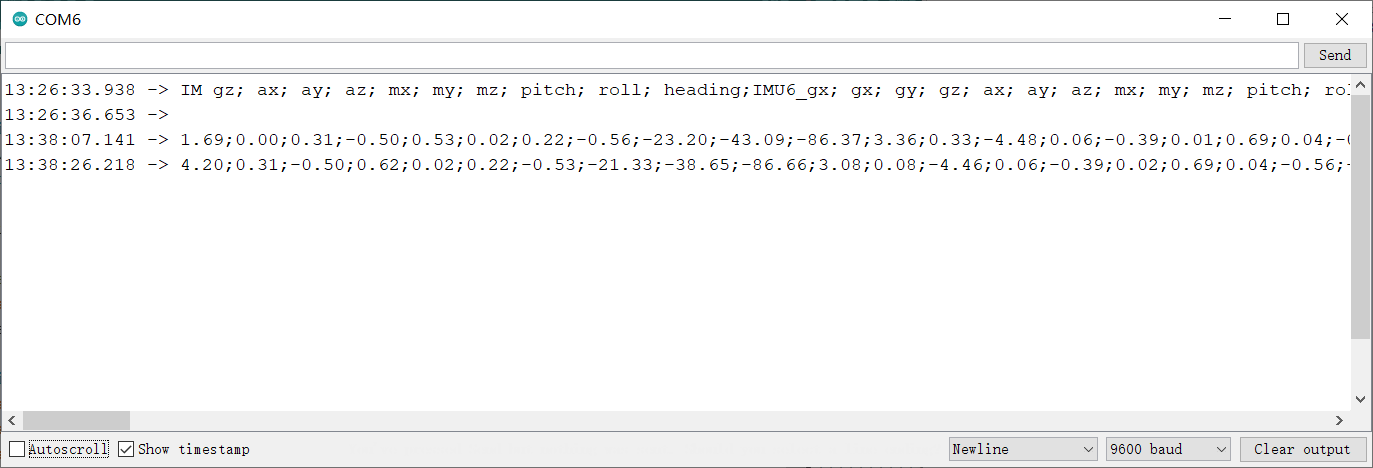
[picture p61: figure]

Mode2

To improve the data printing speed, we can connect the Transmitter (Arduino Mega2560) to the laptop. Other operations of this mode are the same as mode 1, the difference is that we don’t use the receiver Arduino. The code used is the second one.

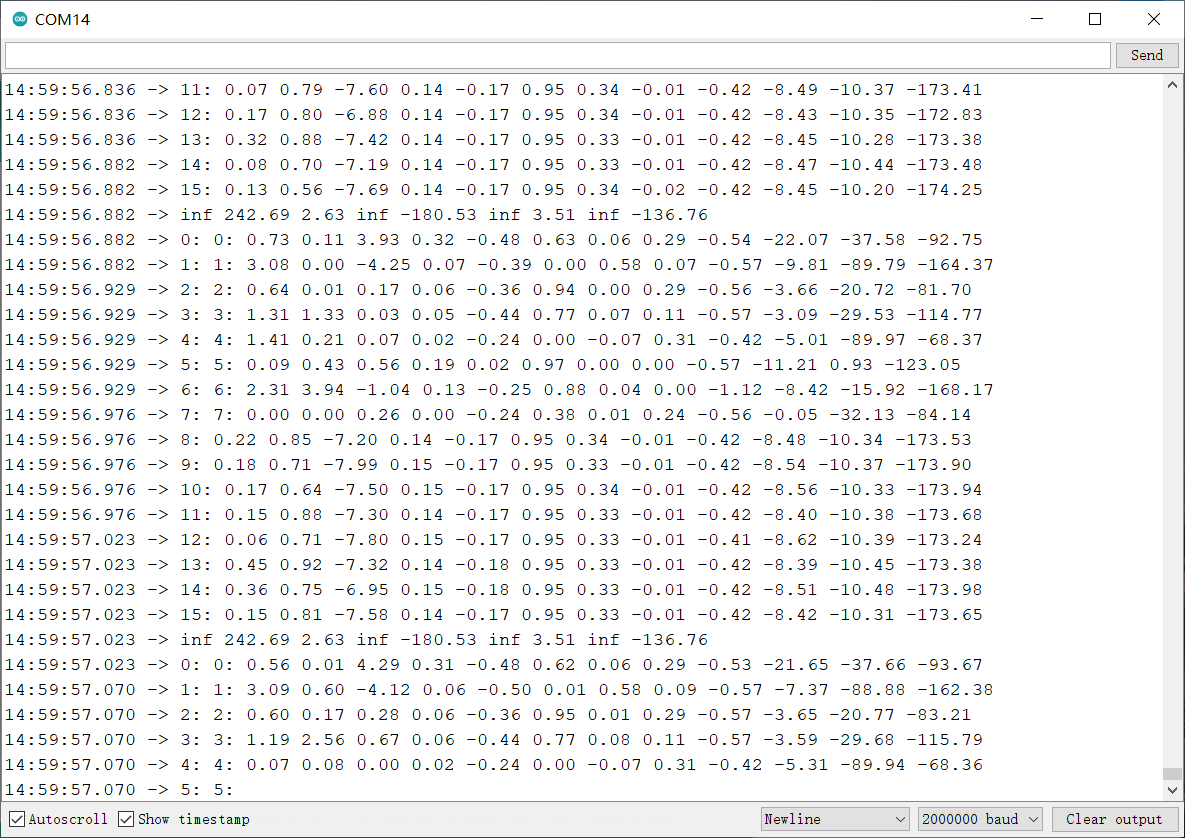
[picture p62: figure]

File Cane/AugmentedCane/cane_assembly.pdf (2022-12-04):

Assembly instructions for the Augmented Cane:

See the components in the bill of materials listed in the repository to ensure you purchase the correct components.

Setting up software on the Raspberry Pi: The open-source software uses a Raspberry Pi image which can be downloaded from our repository. (https://doi.org/10.5281/zenodo.5508346) This image contains the operating system and code that will run on the Rasberry Pi. Once downloaded, unzip the image file (approximately 32 GB in size). Insert your microSD card into your computer using the SD card adapter. We will transfer the image to the microSD card using a free program called balenaEtcher. (https://www.balena.io/etcher/) Install this software and open it. Select the image location that you downloaded, select the microSD card as the drive to install to, and click “Flash!”. Once this has completed, you can eject the microSD card and insert it into the Raspberry Pi. You have finished installing the software and are ready to assemble the hardware.

Building the hardware:

1. To connect the camera to the Raspberry Pi, please see the Raspberry Pi Foundation instructions: https://projects.raspberrypi.org/en/projects/getting-started-with-picamera
2. To connect the RPLIDAR to the Raspberry Pi, simply plug the USB connector into the Raspberry Pi as shown in the image below.

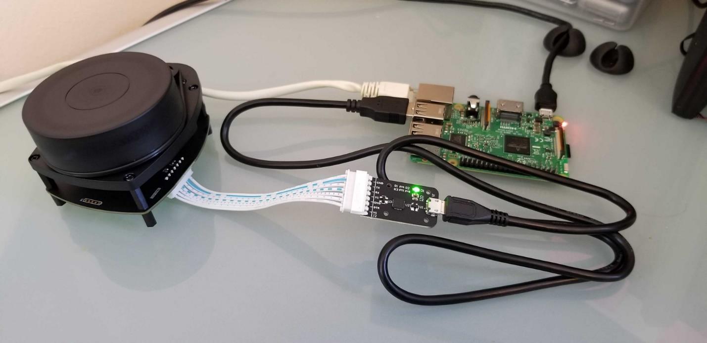
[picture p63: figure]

3. To connect the GPS breakout board to the Raspberry Pi, you will need to solder the VIN, GND, TX, RX pins on the GPS board to the 5V, GND, RX, TX pins on the Adafruit protohat board that will be connected to the Raspberry PI. The RX and TX should be connected to the opposite pins (RX is receive for GPS board, but TX (transmit) for the Pi). See example wiring info here: https://learn.adafruit.com/adafruit-ultimate-gps/circuitpython-parsing
a. To see an example of hot the protohat can be used with the Raspberry Pi, check out this Adafruit project: https://learn.adafruit.com/reef-pi-power-controller
4. To connect the IMU breakout board you will need to solder the VIN, GND, SCL, SDA pins on the IMU board to the 5V, GND, SCL, SDA pins on the Adafruit protohat.

5. The motor controller should be soldered following these instructions: https://learn.adafruit.com/adafruit-drv8871-brushed-dc-motor-driver-breakout/
a. Please note that the power for the motor will be supplied from the LiPo battery on the bill of materials. DO NOT DIRECTLY SOLDER THE BATTERY TO THE POWER PINS. Solder a connector to the power pins so the battery can be disconnected.
6. The pushbutton used to turn off the motor during operation (option for use) should have one end soldered to the #18 pin on the Adafruit protohat and the other pin soldered to 3.3V.
7. The Raspberry Pi will be powered by the rechargeable battery connected into the Raspberry Pi USB-C port.
8. The Raspberry Pi should be protected with the provided case in the bill of materials. The cobbler breakout allows the Adafruit protohat board to be attached to the Raspberry Pi while it is in the case. For attaching all the sensors to the cane you can 3D print the shell housing (STL file in the repository) either with a local 3D printer or using an online service such as Protolabs. (https://www.protolabs.com/) I have uploaded the shell file to Shapeways to make it easy to order directly to your house: https://www.shapeways.com/product/CSHCYNAWM/augmented-cane-3d-printed-shell
a. The components that do not mount to the 3D printed shell (batteries, etc) can be attached to the Raspberry Pi case inside the shell with tape or Velcro. I’ve attached additional images of the assembly to help with this process.

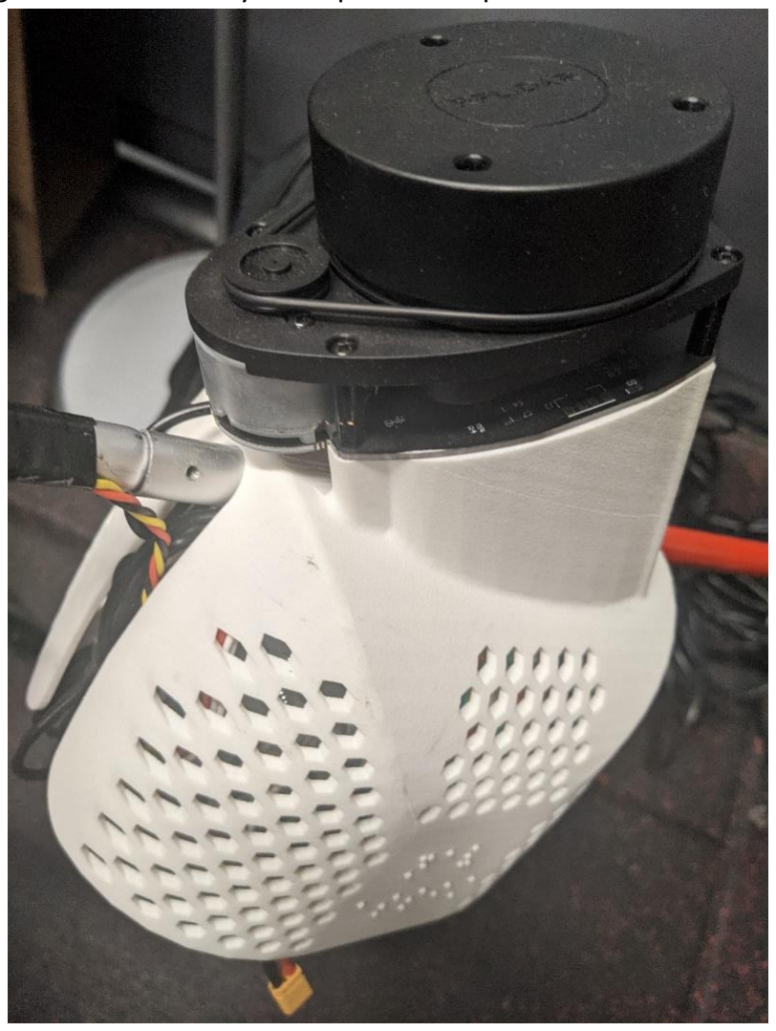
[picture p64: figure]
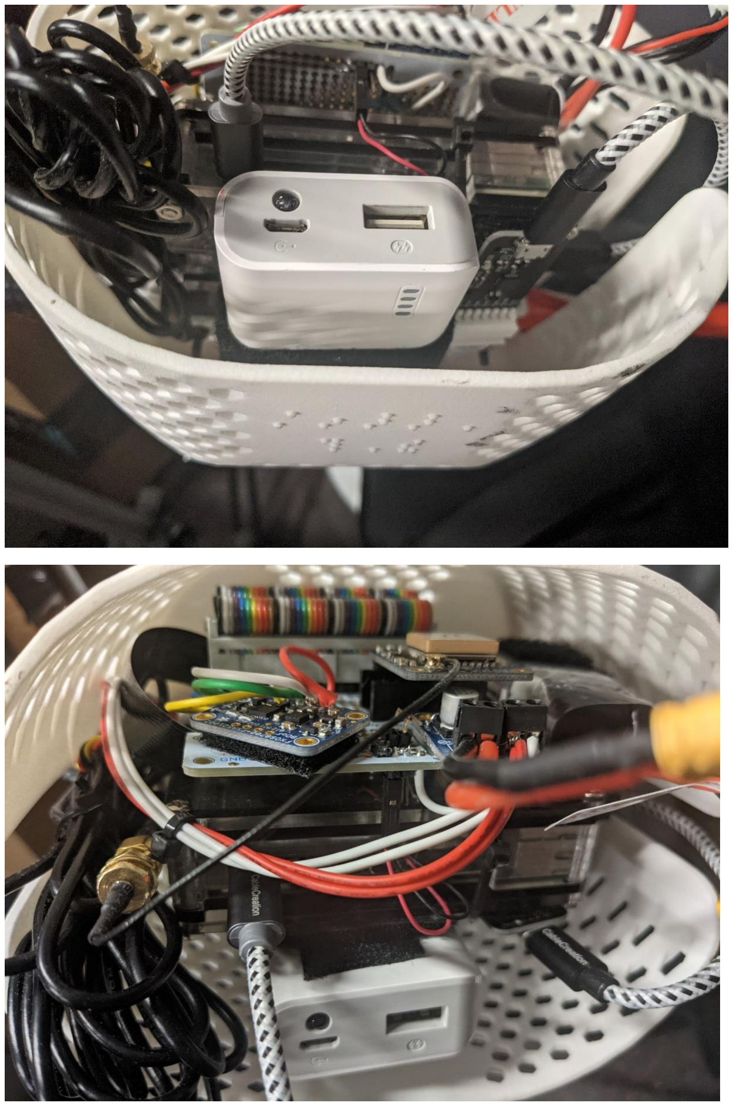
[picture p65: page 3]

9. Assembling the omniwheel and motor assembly will require a hand drill. Drill a hole in the end of the cane. Assemble the motor, two aluminum mounting hubs, omniwheel, and 4mm shaft as shown in the image below.

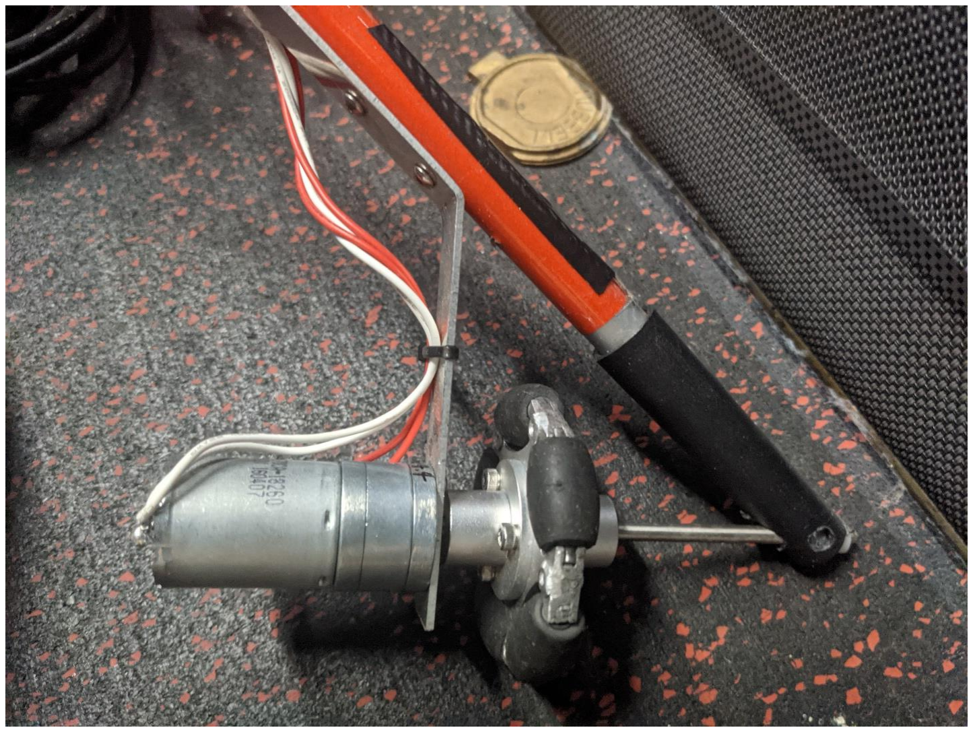
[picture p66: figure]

10. You can run the different programs already installed by using the command line to navigate to the correct directory and entering the following commands:
a. sudo python3 obstacle_avoidance.py
b. sudo python3 gps_navigation.py

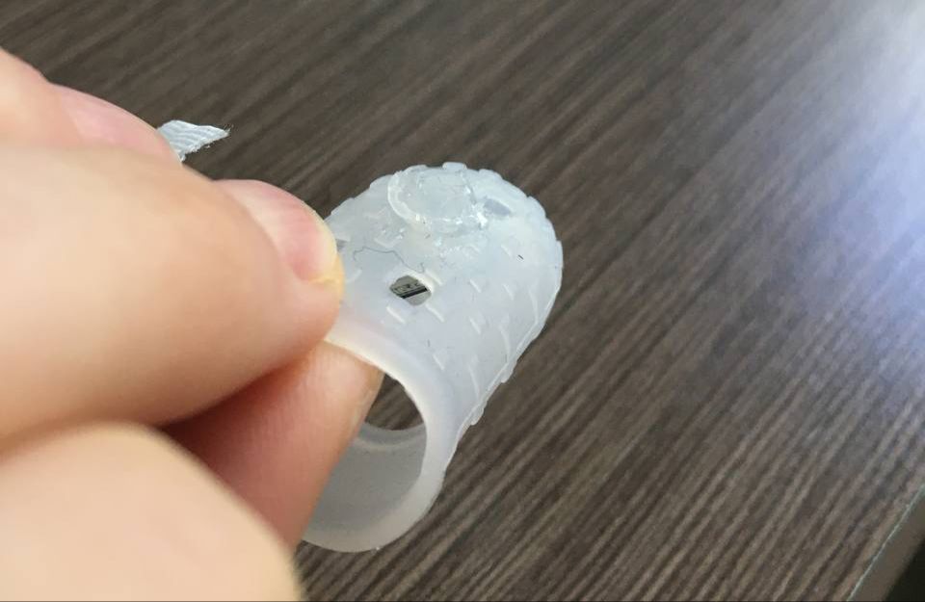
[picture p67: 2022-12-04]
Prosthetic Hand/Multimedia/FSR/FSR_setup_idea2.jpeg

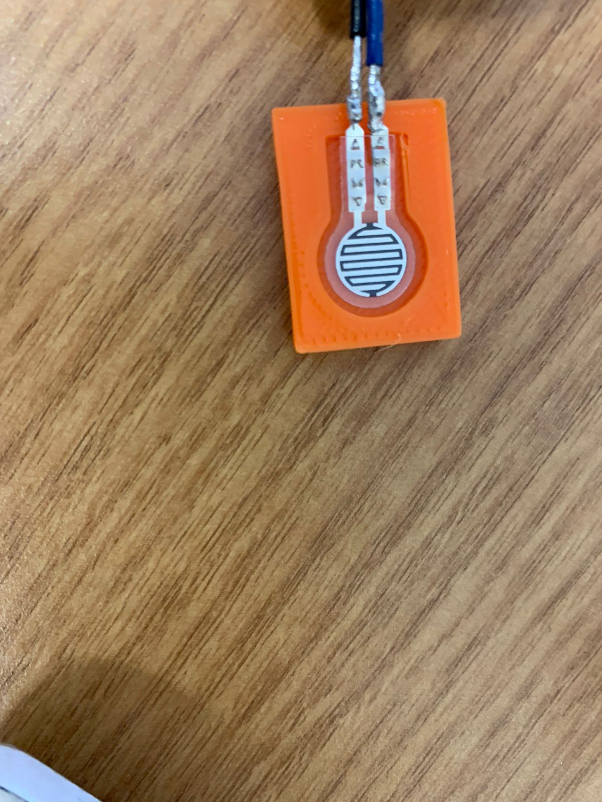
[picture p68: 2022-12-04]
Prosthetic Hand/Multimedia/FSR/setup_fsr4.jpeg

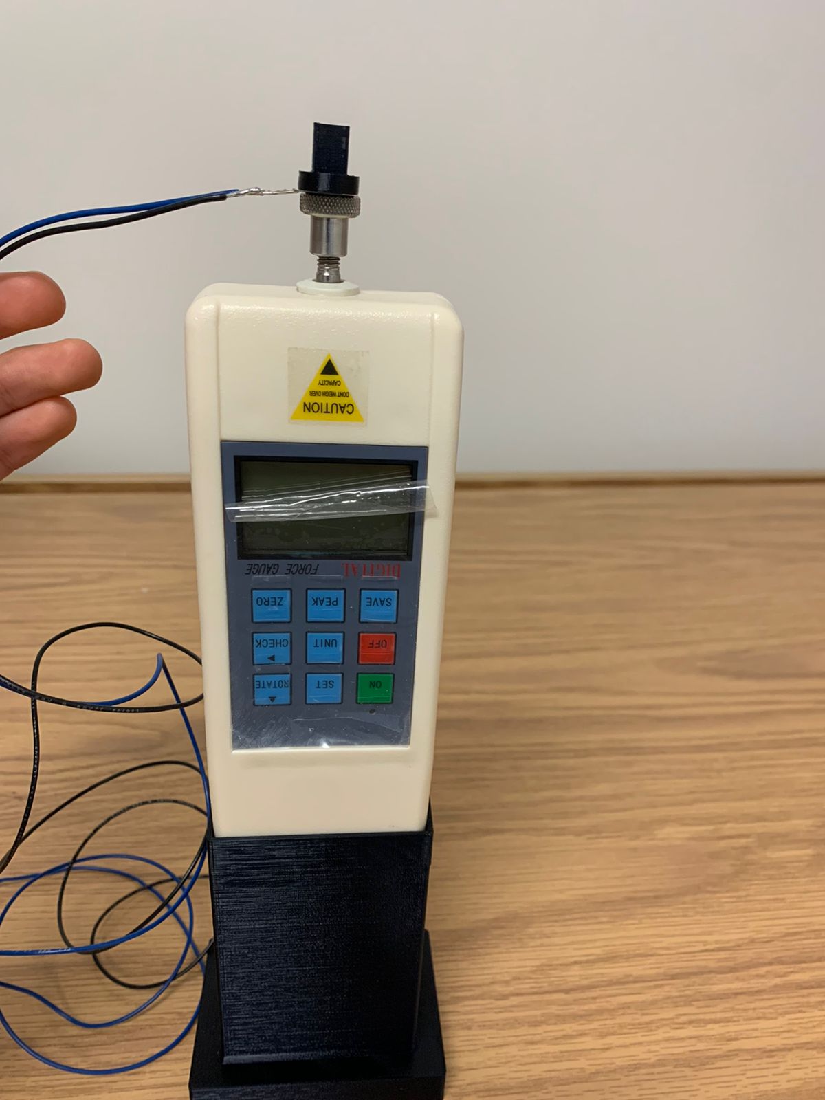
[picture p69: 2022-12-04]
Prosthetic Hand/Multimedia/FSR/setup_fsr1.jpeg

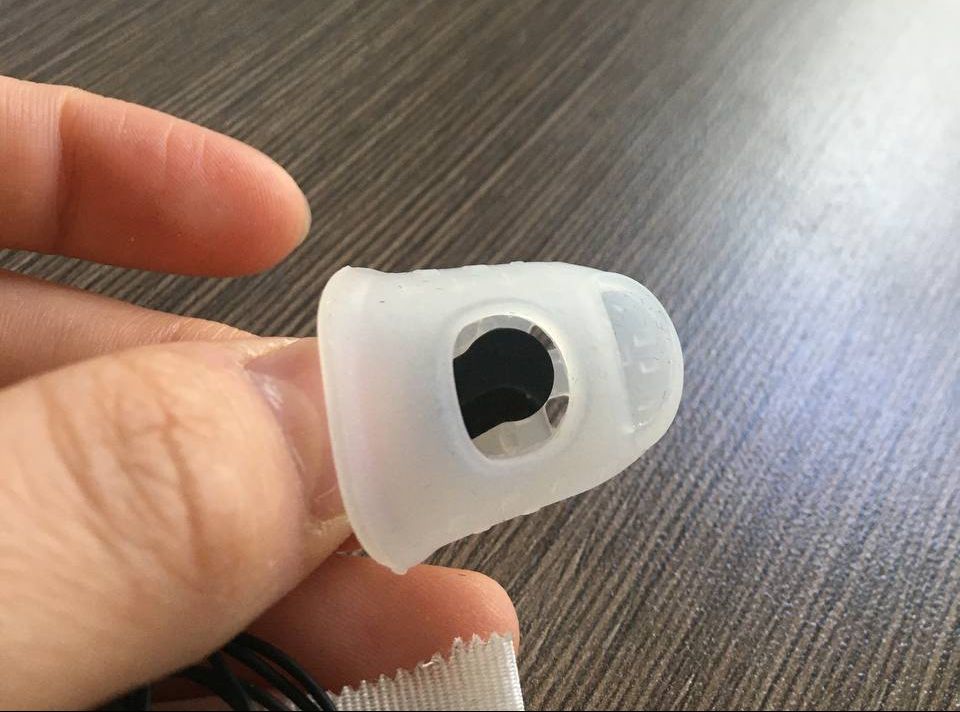
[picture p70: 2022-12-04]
Prosthetic Hand/Multimedia/FSR/FSR_setup_idea1.jpeg

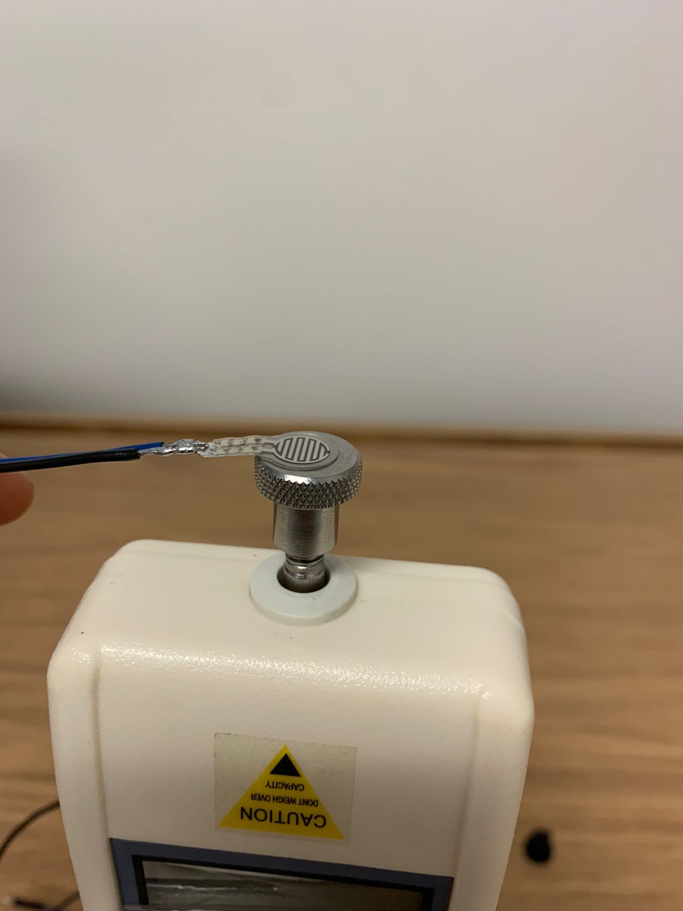
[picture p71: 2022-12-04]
Prosthetic Hand/Multimedia/FSR/setup_fsr2.jpeg

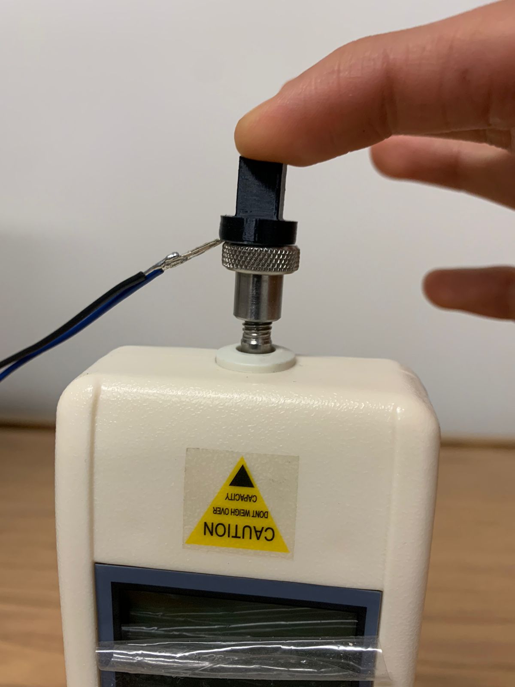
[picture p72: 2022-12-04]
Prosthetic Hand/Multimedia/FSR/setup_fsr3.jpeg

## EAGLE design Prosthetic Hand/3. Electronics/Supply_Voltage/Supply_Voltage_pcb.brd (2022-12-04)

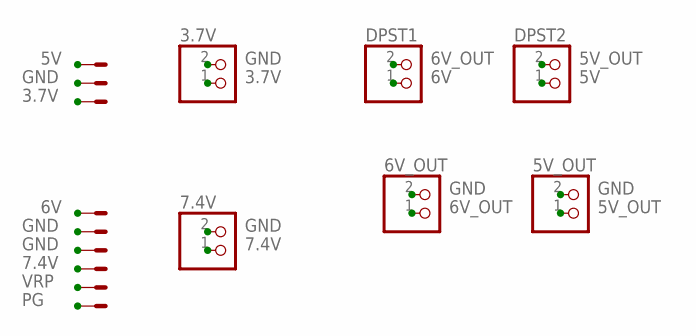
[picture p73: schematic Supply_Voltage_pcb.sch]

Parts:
3.7V, 5V_OUT, 6V_OUT, 7.4V: JST_2PIN-THM; JST-PH-2-THM
DPST1, DPST2: JST_2PIN-THM; JST-PH-2-THM
VC-3.7V-5V: 22-23-2031
VC-7.4V-6V: 22-23-2061

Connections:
3.7V: 3.7V.1 (2), VC-3.7V-5V.3
5V: DPST2.1 (2), VC-3.7V-5V.1
5V_OUT: 5V_OUT.1 (2), DPST2.2 (1)
6V: DPST1.1 (2), VC-7.4V-6V.1
6V_OUT: 6V_OUT.1 (2), DPST1.2 (1)
7.4V: 7.4V.1 (2), VC-7.4V-6V.4
GND: 3.7V.2 (1), 5V_OUT.2 (1), 6V_OUT.2 (1), 7.4V.2 (1), VC-3.7V-5V.2, VC-7.4V-6V.2, VC-7.4V-6V.3
PG: VC-7.4V-6V.6
VRP: VC-7.4V-6V.5

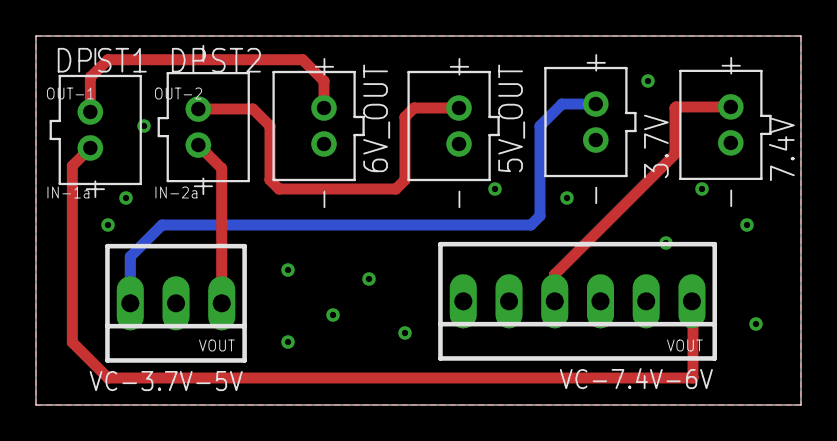
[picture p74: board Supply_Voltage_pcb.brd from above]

Board: 2 copper layers, 42.5 x 20.5 mm, 8 parts (0 on the bottom side), 7 nets.

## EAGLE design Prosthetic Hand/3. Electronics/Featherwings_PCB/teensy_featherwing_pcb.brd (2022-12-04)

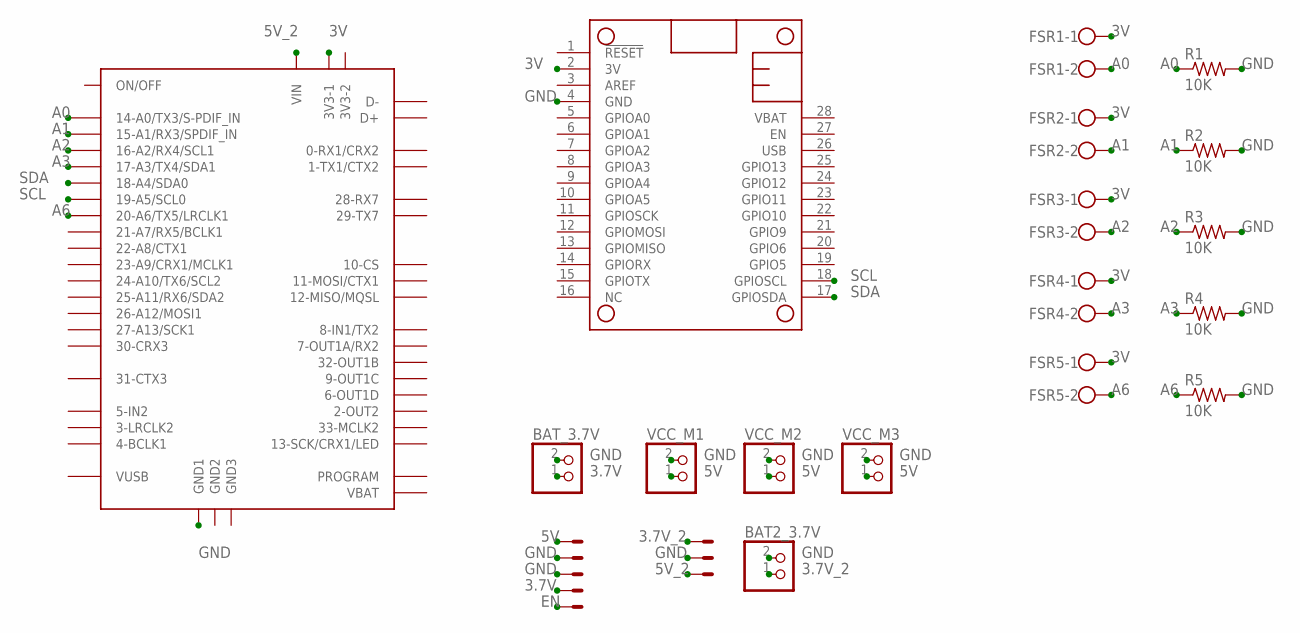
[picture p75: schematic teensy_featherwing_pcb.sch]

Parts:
5V_1A: 22-23-2031
5V_3A: 22-23-2051
BAT2_3.7V: JST_2PIN-THM; JST-PH-2-THM
BAT_3.7V: JST_2PIN-THM; JST-PH-2-THM
DC_MOTOR_DRIVER: FEATHERWING_NODIM; FEATHERWING_DIM
FSR1, FSR2, FSR3, FSR4, FSR5: W237-102
R1, R2, R3, R4, R5: 10K; 0207/10
U$1: TEENSY40
VCC_M1, VCC_M2, VCC_M3: JST_2PIN-THM; JST-PH-2-THM

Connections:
3.7V: 5V_3A.4, BAT_3.7V.1 (2)
3.7V_2: 5V_1A.1, BAT2_3.7V.1 (2)
3V: DC_MOTOR_DRIVER.2 (3V), FSR1.1, FSR2.1, FSR3.1, FSR4.1, FSR5.1, U$1.3V3-1
5V: 5V_3A.1, VCC_M1.1 (2), VCC_M2.1 (2), VCC_M3.1 (2)
5V_2: 5V_1A.3, U$1.VIN
A0: FSR1.2, R1.1, U$1.14-A0/TX3/S-PFI_OUT (14-A0/TX3/S-PDIF_IN)
A1: FSR2.2, R2.1, U$1.15-A1/RX3/S-PDIF_IN (15-A1/RX3/SPDIF_IN)
A2: FSR3.2, R3.1, U$1.16-A2/RX4/SCL1
A3: FSR4.2, R4.1, U$1.17-A3/TX4/SDA1
A6: FSR5.2, R5.1, U$1.20-A6/TX5/LRCLK1
EN: 5V_3A.5
GND: 5V_1A.2, 5V_3A.2, 5V_3A.3, BAT2_3.7V.2 (1), BAT_3.7V.2 (1), DC_MOTOR_DRIVER.4 (GND), R1.2, R2.2, R3.2, R4.2, R5.2, U$1.GND1, VCC_M1.2 (1), VCC_M2.2 (1), VCC_M3.2 (1)
SCL: DC_MOTOR_DRIVER.18 (GPIOSCL), U$1.19-A5/SCL0
SDA: DC_MOTOR_DRIVER.17 (GPIOSDA), U$1.18-A4/SDA0

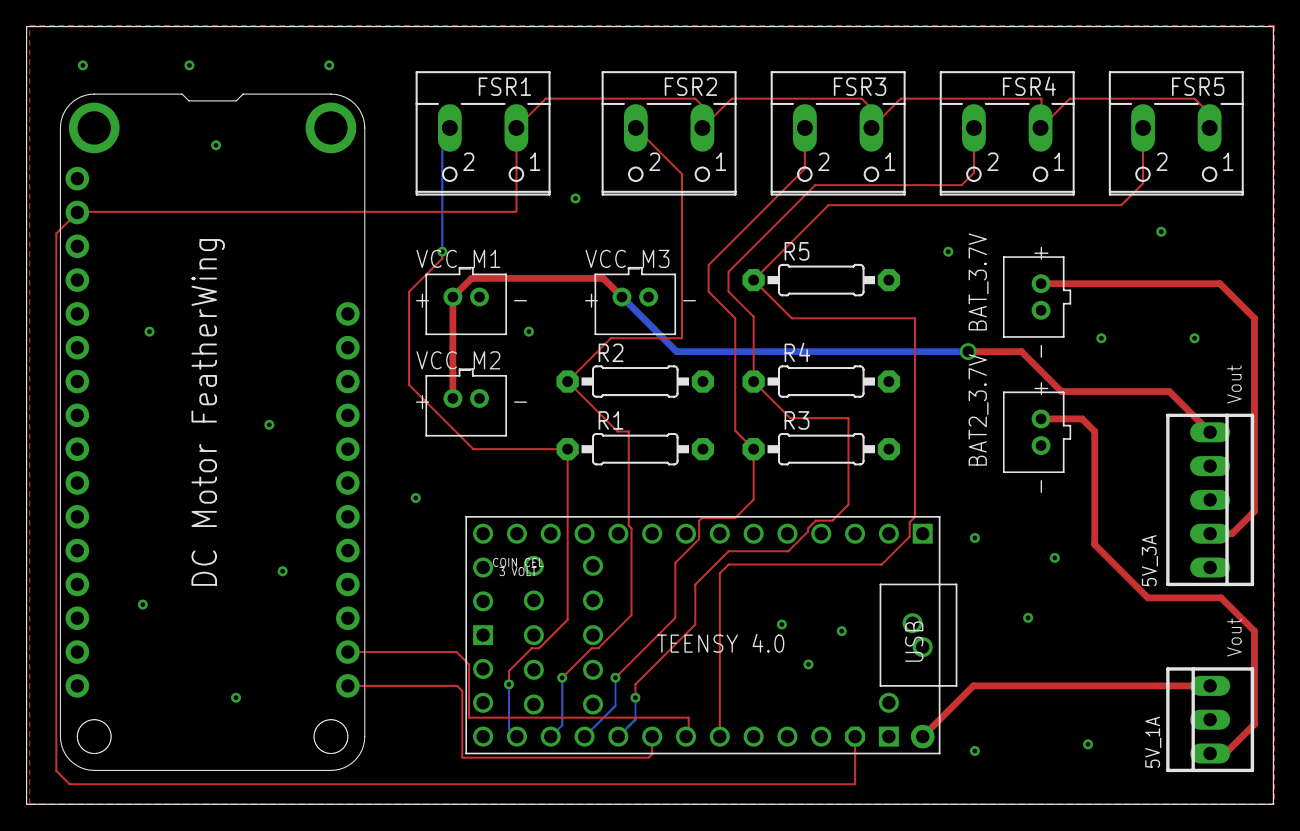
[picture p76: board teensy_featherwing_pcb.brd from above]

Board: 2 copper layers, 93.7 x 58.4 mm, 19 parts (0 on the bottom side), 13 nets.

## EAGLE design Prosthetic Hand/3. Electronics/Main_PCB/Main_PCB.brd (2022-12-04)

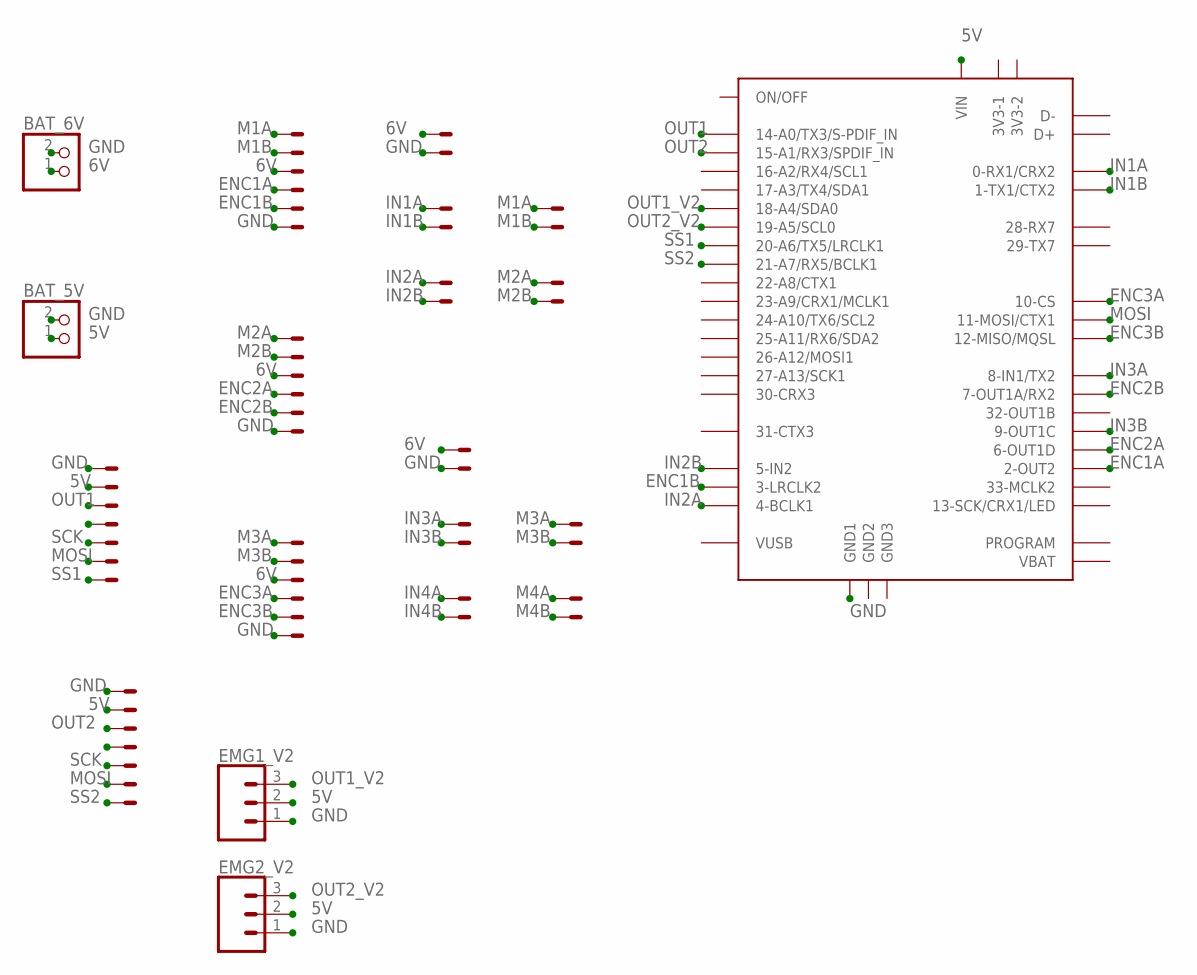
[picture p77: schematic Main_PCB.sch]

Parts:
BAT_5V, BAT_6V: JST_2PIN-THM; JST-PH-2-THM
EMG1, EMG2: 53047-07
EMG1_V2, EMG2_V2: CONN_03; 1X03
JST-M1, JST-M2, JST-M3: 22-23-2061
MD1-IN1, MD1-IN2, MD1-M1, MD1-M2, MD1-PWR, MD2-IN3, MD2-IN4, MD2-M3, MD2-M4, MD2-PWR: 22-23-2021
U$1: TEENSY40

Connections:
5V: BAT_5V.1 (2), EMG1.2, EMG1_V2.2, EMG2.2, EMG2_V2.2, U$1.VIN
6V: BAT_6V.1 (2), JST-M1.3, JST-M2.3, JST-M3.3, MD1-PWR.1, MD2-PWR.1
ENC1A: JST-M1.4, U$1.2-OUT2
ENC1B: JST-M1.5, U$1.3-LRCLK2
ENC2A: JST-M2.4, U$1.6-OUT1D
ENC2B: JST-M2.5, U$1.7-RX2/OUT1A (7-OUT1A/RX2)
ENC3A: JST-M3.4, U$1.10-CS/MQSR (10-CS)
ENC3B: JST-M3.5, U$1.12-MIO/MQSL (12-MISO/MQSL)
GND: BAT_5V.2 (1), BAT_6V.2 (1), EMG1.1, EMG1_V2.1, EMG2.1, EMG2_V2.1, JST-M1.6, JST-M2.6, JST-M3.6, MD1-PWR.2, MD2-PWR.2, U$1.GND1
IN1A: MD1-IN1.1, U$1.0-RX1 (0-RX1/CRX2)
IN1B: MD1-IN1.2, U$1.1-TX1 (1-TX1/CTX2)
IN2A: MD1-IN2.1, U$1.4-BCLK2 (4-BCLK1)
IN2B: MD1-IN2.2, U$1.5-IN2
IN3A: MD2-IN3.1, U$1.8-TX2/IN1 (8-IN1/TX2)
IN3B: MD2-IN3.2, U$1.9-OUT1C
IN4A: MD2-IN4.1
IN4B: MD2-IN4.2
M1A: JST-M1.1, MD1-M1.1
M1B: JST-M1.2, MD1-M1.2
M2A: JST-M2.1, MD1-M2.1
M2B: JST-M2.2, MD1-M2.2
M3A: JST-M3.1, MD2-M3.1
M3B: JST-M3.2, MD2-M3.2
M4A: MD2-M4.1
M4B: MD2-M4.2
MOSI: EMG1.6, EMG2.6, U$1.11-MOSI/CTX1
OUT1: EMG1.3, U$1.14-A0/TX3/S-PFI_OUT (14-A0/TX3/S-PDIF_IN)
OUT1_V2: EMG1_V2.3, U$1.18-A4/SDA0
OUT2: EMG2.3, U$1.15-A1/RX3/S-PDIF_IN (15-A1/RX3/SPDIF_IN)
OUT2_V2: EMG2_V2.3, U$1.19-A5/SCL0
SCK: EMG1.5, EMG2.5
SS1: EMG1.7, U$1.20-A6/TX5/LRCLK1
SS2: EMG2.7, U$1.21-A7/RX5/BCLK1

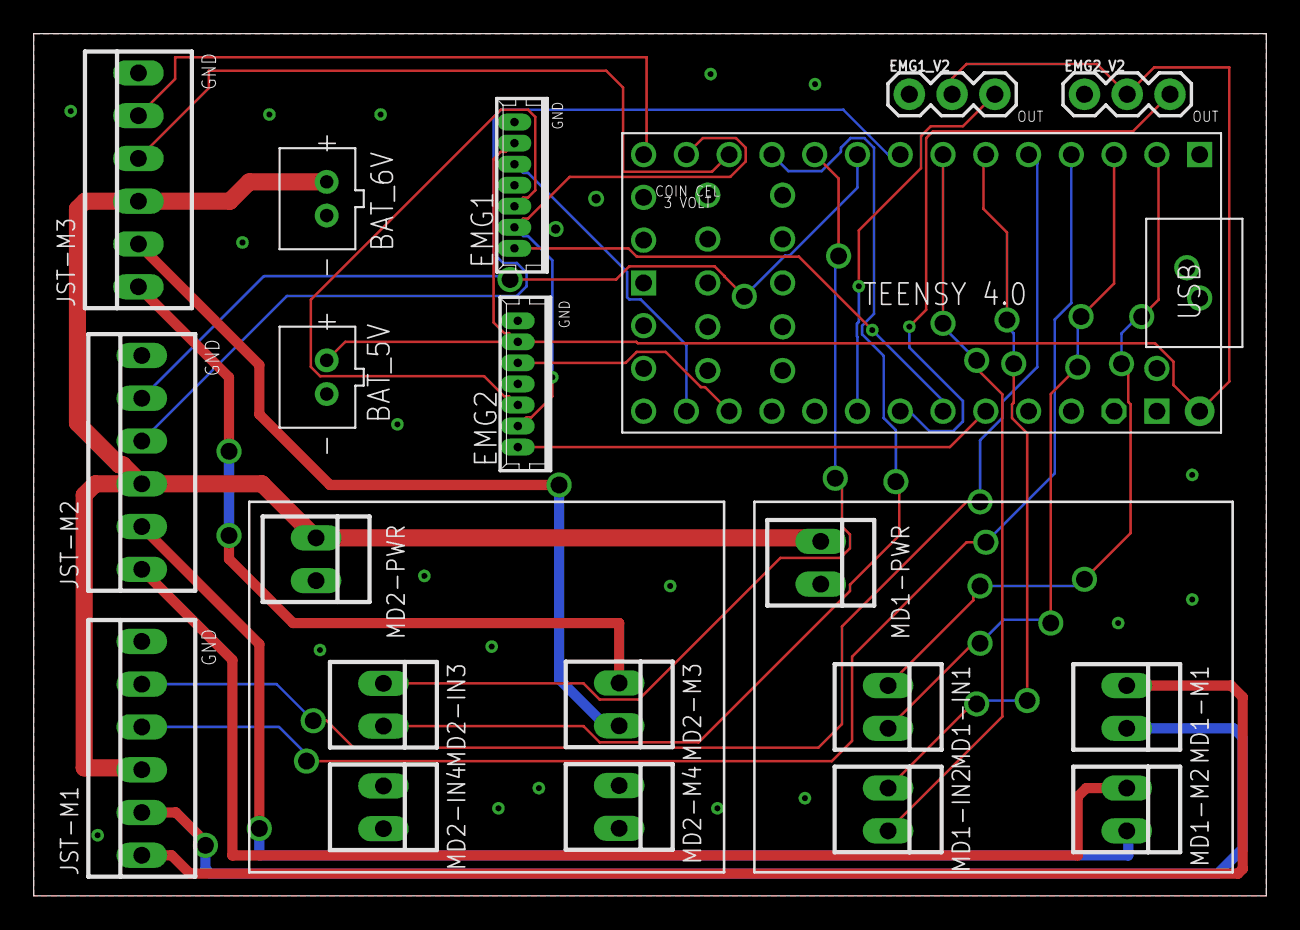
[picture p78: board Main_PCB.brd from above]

Board: 2 copper layers, 73.2 x 51.2 mm, 20 parts (0 on the bottom side), 29 nets.

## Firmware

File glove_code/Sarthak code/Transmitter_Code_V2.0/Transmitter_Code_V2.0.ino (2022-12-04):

#include <RH_ASK.h>
#include <SPI.h>
#include <LSM9DS1_Registers.h>
#include <LSM9DS1_Types.h>
#include <SparkFunLSM9DS1.h>
#include <Wire.h>
#include <stdio.h> 

LSM9DS1 imu[16];

#define TCAADDR  0x70 
#define TCAADDR2 0x71   //enable the A0 Pin on the second TCA
#define num 16;     //the number of the IMUs

int sen1=A0;
int sen2=A1;
int sen3=A2;
int sen4=A3;
int sen5=A10;
int sen6=A11;
int sen7=A12;
int sen8=A13;
int sen9=A14;


float zeroVal1=0;
float zeroVal2=0;
float zeroVal3=0;
float zeroVal4=0;
float zeroVal5=0;
float zeroVal6=0;
float zeroVal7=0;
float zeroVal8=0;
float zeroVal9=0;


float ninetyVal1=0;
float ninetyVal2=0;
float ninetyVal3=0;
float ninetyVal4=0;
float ninetyVal5=0;
float ninetyVal6=0;
float ninetyVal7=0;
float ninetyVal8=0;
float ninetyVal9=0;

float imu_gx[16];
float imu_gy[16];
float imu_gz[16];
float imu_ax[16];
float imu_ay[16];
float imu_az[16];
float imu_mx[16];
float imu_my[16];
float imu_mz[16];


int loops=100;


int initalDelay=500;
int delayTime=50;     //100;


int VCC=5.15;


int button1=4;
int button2=8;
int ledPin=12;


int delayDebounce=50;


float sum1=0;
float sum2=0;
float sum3=0;
float sum4=0;
float sum5=0;
float sum6=0;
float sum7=0;
float sum8=0;
float sum9=0;


float val0;
float val1;
float val2;
float val3;
float val4;
float val5;
float val6;
float val7;
float val8;
float val9;


int checkZero=LOW;
int checkNinety=LOW;


float data0;
float data1;
float data2;
float data3;
float data4;
float data5;
float data6;
float data7;
float data8;
float data9;


RH_ASK driver(2000,11,50);

////////////////use to select the tca multiplexers used///////////////////

void tcaselect (uint8_t i) { 

  if (i > num-1 ) return ;
  if (i<8){
  Wire.beginTransmission(TCAADDR); 
  Wire.write(1 << i); 
  Wire.endTransmission(); 
  Serial.print(i);
  Serial.print(": ");
  }
  
  if (7<i<16){
  Wire.beginTransmission(TCAADDR2); 
  Wire.write(1 << i); 
  Wire.endTransmission(); 
  Serial.print(i);
  Serial.print(": ");
  }
}

////////////////////////////
// Sketch Output Settings //
////////////////////////////
#define PRINT_CALCULATED
#define PRINT_SPEED 5 // 100 ms between prints
static unsigned long lastPrint = 0;   // Keep track of print time
#define DECLINATION -8.58             // Declination (degrees) in Boulder, CO.
void printGyro1();
void printAccel1();
void printMag1();
void printAttitude(float ax, float ay, float az, float mx, float my, float mz);


void setup() {
 Serial.begin(115200);
  pinMode(sen1,INPUT);
  pinMode(sen2,INPUT);
  pinMode(sen3,INPUT);
  pinMode(sen4,INPUT);
  pinMode(sen5,INPUT);
  pinMode(sen6,INPUT);
  pinMode(sen7,INPUT);
  pinMode(sen8,INPUT);
  pinMode(sen9,INPUT);

 
  pinMode(button1,INPUT);
  pinMode(button2,INPUT);
  pinMode(ledPin,OUTPUT);

Wire.begin();
for(int n=0;n<num;n++){
  tcaselect(n);
  #define LSM9DS1_M   0x1E // Would be 0x1C if SDO_M is LOW
  #define LSM9DS1_AG  0x6B // Would be 0x6A if SDO_AG is LOW
imu[n].settings.device.commInterface = IMU_MODE_I2C; // Set mode to I2C
imu[n].settings.device.mAddress = LSM9DS1_M; // Set mag address to 0x1E
imu[n].settings.device.agAddress = LSM9DS1_AG; // Set ag address to 0x6B

  if (imu[n].begin() == false) // with no arguments, this uses default addresses (AG:0x6B, M:0x1E) and i2c port (Wire).
  {
    Serial.println("Failed to communicate with the LSM9DS1.");
    Serial.println("Double-check wiring.");
    Serial.println("Default settings in this sketch will " \
                   "work for an out of the box LSM9DS1 " \
                   "Breakout, but may need to be modified " \
                   "if the board jumpers are.");
    while (1);
  }
 }

  driver.init();
  
  if (!driver.init()){
    Serial.println("Driver init failed");
  }
  
}

void loop() {
  
//////////////////////////the button1(yellow one) been pushed/////////////////////////////////

if(digitalRead(button1)==LOW && digitalRead(button2)==HIGH && checkZero==LOW){
    delay(delayDebounce);
   
    if(digitalRead(button1)==LOW && digitalRead(button2)==HIGH){
  
  digitalWrite(ledPin,HIGH);
  delay(initalDelay);
  
  for(int i=0;i<loops;i++){
    zeroVal1=zeroVal1 + (analogRead(sen1)*VCC)/1023.0;
    zeroVal2=zeroVal2 + (analogRead(sen2)*VCC)/1023.0;
    zeroVal3=zeroVal3 + (analogRead(sen3)*VCC)/1023.0;
    zeroVal4=zeroVal4 + (analogRead(sen4)*VCC)/1023.0;
    zeroVal5=zeroVal5 + (analogRead(sen5)*VCC)/1023.0;
    zeroVal6=zeroVal6 + (analogRead(sen6)*VCC)/1023.0;
    zeroVal7=zeroVal7 + (analogRead(sen7)*VCC)/1023.0;
    zeroVal8=zeroVal8 + (analogRead(sen8)*VCC)/1023.0;
    zeroVal9=zeroVal9 + (analogRead(sen9)*VCC)/1023.0;
    delay(delayTime);
  }

    zeroVal1=zeroVal1/loops;
    zeroVal2=zeroVal2/loops;
    zeroVal3=zeroVal3/loops;
    zeroVal4=zeroVal4/loops;
    zeroVal5=zeroVal5/loops;
    zeroVal6=zeroVal6/loops;
    zeroVal7=zeroVal7/loops;
    zeroVal8=zeroVal8/loops;
    zeroVal9=zeroVal9/loops;
    
   checkZero=HIGH;
   Serial.println("");  
   Serial.println("The zero angle value has been set.");
   Serial.println(zeroVal7);
  
//   const char *msg1 = "The zero degree angle value has been set.";
//   driver.send((uint8_t *)msg1, strlen(msg1));
//   driver.waitPacketSent();
//   //Serial.println("Hello World");
//   //delay(100);

    digitalWrite(ledPin,LOW);
 }
}

//////////////////////////the button2(green one) been pushed/////////////////////////////////

if(digitalRead(button2)==LOW && digitalRead(button1)==HIGH && checkNinety==LOW){
    delay(delayDebounce);
    if(digitalRead(button2)==LOW && digitalRead(button1)==HIGH){
  
 
  digitalWrite(ledPin,HIGH);
  delay(initalDelay);
  
  for(int i=0;i<loops;i++){
    ninetyVal1=ninetyVal1 + (analogRead(sen1)*VCC)/1023.0;
    ninetyVal2=ninetyVal2 + (analogRead(sen2)*VCC)/1023.0;
    ninetyVal3=ninetyVal3 + (analogRead(sen3)*VCC)/1023.0;
    ninetyVal4=ninetyVal4 + (analogRead(sen4)*VCC)/1023.0;
    ninetyVal5=ninetyVal5 + (analogRead(sen5)*VCC)/1023.0;
    ninetyVal6=ninetyVal6 + (analogRead(sen6)*VCC)/1023.0;
    ninetyVal7=ninetyVal7 + (analogRead(sen7)*VCC)/1023.0;
    ninetyVal8=ninetyVal8 + (analogRead(sen8)*VCC)/1023.0;
    ninetyVal9=ninetyVal9 + (analogRead(sen9)*VCC)/1023.0;
    delay(delayTime);
  }

    ninetyVal1=ninetyVal1/loops;
    ninetyVal2=ninetyVal2/loops;
    ninetyVal3=ninetyVal3/loops;
    ninetyVal4=ninetyVal4/loops;
    ninetyVal5=ninetyVal5/loops;
    ninetyVal6=ninetyVal6/loops;
    ninetyVal7=ninetyVal7/loops;
    ninetyVal8=ninetyVal8/loops;
    ninetyVal9=ninetyVal9/loops;
  
  checkNinety=HIGH; 
  Serial.println("The ninety angle value has been set.");
  
//  const char *msg2 = "The ninety degree angle value has been set.";
//  driver.send((uint8_t *)msg2, strlen(msg2));
//  driver.waitPacketSent();
//  //Serial.println("Hello World");
//  //delay(100);

    digitalWrite(ledPin,LOW); 
 }
}
////////////////////////////////////////////////////////////////////////////////
/***************** two buttons been pushed,start collecting data **************/
////////////////////////////////////////////////////////////////////////////////

if(digitalRead(button1)==LOW && digitalRead(button2)==LOW){
  delay(delayDebounce);
  if(digitalRead(button1)==LOW && digitalRead(button2)==LOW){
    if(checkZero==HIGH && checkNinety==HIGH){

  //Serial.println("started collecting data");
  digitalWrite(ledPin,HIGH);
  delay(70);
  digitalWrite(ledPin,LOW);
  delay(70);
  digitalWrite(ledPin,HIGH);
  delay(70);
  digitalWrite(ledPin,LOW);
  delay(70);
  digitalWrite(ledPin,HIGH);
  delay(70);
  digitalWrite(ledPin,LOW);
  delay(70);
  digitalWrite(ledPin,HIGH);
  delay(70);
  digitalWrite(ledPin,LOW);
  delay(70);
  digitalWrite(ledPin,HIGH);
  delay(70);
  digitalWrite(ledPin,LOW);
  while(1!=0){
  sum1=0;
  sum2=0;
  sum3=0;
  sum4=0;
  sum5=0;
  sum6=0;
  sum7=0;
  sum8=0;
  sum9=0;

  delay(initalDelay);
//for(int i=0;i<loops;i++){
    sum1=sum1 + (analogRead(sen1)*VCC)/1023.0;
    sum2=sum2 + (analogRead(sen2)*VCC)/1023.0;
    sum3=sum3 + (analogRead(sen3)*VCC)/1023.0;
    sum4=sum4 + (analogRead(sen4)*VCC)/1023.0;
    sum5=sum5 + (analogRead(sen5)*VCC)/1023.0;
    sum6=sum6 + (analogRead(sen6)*VCC)/1023.0;
    sum7=sum7 + (analogRead(sen7)*VCC)/1023.0;
    sum8=sum8 + (analogRead(sen8)*VCC)/1023.0;
    sum9=sum9 + (analogRead(sen9)*VCC)/1023.0;
    //delay(delayTime);
//  }

/////////////////////////// IMU data read and send////////////////////////

int t=0;
//char imu_begin_sending='y';
//  driver.send((char *)&imu_begin_sending, sizeof(imu_begin_sending));
//  driver.waitPacketSent();
  
for(;t<num;t++){
  tcaselect(t);
if ( imu[t].gyroAvailable() )
    imu[t].readGyro();
  if ( imu[t].accelAvailable() )
    imu[t].readAccel();
  if ( imu[t].magAvailable() )
    imu[t].readMag();

  if ((lastPrint + PRINT_SPEED) < millis())
  {
    printGyro1(t);  // Print "G: gx, gy, gz"
    printAccel1(t); // Print "A: ax, ay, az"
    printMag1(t);   // Print "M: mx, my, mz"
    printAttitude(imu[t].ax, imu[t].ay, imu[t].az,
                  -imu[t].my, -imu[t].mx, imu[t].mz);
    Serial.println();
    lastPrint = millis(); // Update lastPrint time
  }
  
  delay(5); 
}

////////////// Serial print and send data to the receiver ///////////

val0=mapf(sum1,zeroVal1,ninetyVal1,0,90.0);
  data0=val0;
//  Serial.print("The angle from the first sensor is: ");
//  Serial.println(data0);
  driver.send((uint8_t *)&data0, sizeof(data0));
  driver.waitPacketSent();
//  Serial.println("sent");
//  delay(100);

val1=mapf(sum1,zeroVal1,ninetyVal1,0,90.0);
  data1=val1;
  Serial.print("The angle from the first sensor is: ");
  Serial.println(data1);
  driver.send((uint8_t *)&data1, sizeof(data1));
  driver.waitPacketSent();
//  delay(100);
  
val2=mapf(sum2,zeroVal2,ninetyVal2,0,90.0);
  data2=val2;
  Serial.print("The angle from the second sensor is: ");
  Serial.println(data2);
  driver.send((uint8_t *)&data2, sizeof(data2));
  driver.waitPacketSent();
//  delay(100);
  
val3=mapf(sum3,zeroVal3,ninetyVal3,0,90.0);
  data3=val3;
  Serial.print("The angle from the third sensor is: ");
  Serial.println(data3);
  driver.send((uint8_t *)&data3, sizeof(data3));
  driver.waitPacketSent();
//  delay(100);
  
val4=mapf(sum4,zeroVal4,ninetyVal4,0,90.0);
  data4=val4;
  Serial.print("The angle from the fourth sensor is: ");
  Serial.println(data4);
  driver.send((uint8_t *)&data4, sizeof(data4));
  driver.waitPacketSent();
//  delay(100);
  
val5=mapf(sum5,zeroVal5,ninetyVal5,0,90.0);
  data5=val5;
  Serial.print("The angle from the fifth sensor is: ");
  Serial.println(data5);
  driver.send((uint8_t *)&data5, sizeof(data5));
  driver.waitPacketSent();
//  delay(100);
  
val6=mapf(sum6,zeroVal6,ninetyVal6,0,90.0);
  data6=val6;
  Serial.print("The angle from the sixth sensor is: ");
  Serial.println(data6);
  driver.send((uint8_t *)&data6, sizeof(data6));
  driver.waitPacketSent();
//  delay(100);
  
val7=mapf(sum7,zeroVal7,ninetyVal7,0,90.0);
  data7=val7;
  Serial.print("The angle from the seventh sensor is: ");
  Serial.println(data7);
  driver.send((uint8_t *)&data7, sizeof(data7));
  driver.waitPacketSent();
//  delay(100);
  
val8=mapf(sum8,zeroVal8,ninetyVal8,0,90.0);
  data8=val8;
  Serial.print("The angle from the eigth sensor is: ");
  Serial.println(data8);
  driver.send((uint8_t *)&data8, sizeof(data8));
  driver.waitPacketSent();
//  delay(100);
  
val9=mapf(sum9,zeroVal9,ninetyVal9,0,90.0);
  data9=val9;
  Serial.print("The angle from the ninth sensor is: ");
  Serial.println(data9);
  driver.send((uint8_t *)&data9, sizeof(data9));
  driver.waitPacketSent();
//  delay(100);

//uint8_t oneturn=0;
//  driver.send((uint8_t *)&oneturn, sizeof(oneturn));
//  driver.waitPacketSent();

  delay(5);
    }
    }
  }
}
}


float mapf(float x, float in_min, float in_max, float out_min, float out_max)
{
  return (x - in_min) * (out_max - out_min) / (in_max - in_min) + out_min;
}


///////////////// functions for the IMUs /////////////////////////
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

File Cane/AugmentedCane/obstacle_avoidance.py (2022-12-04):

## TODO: try and make less brittle by using more sections of lidar for just slight turns rather than whole 90 degree turns
## use more sections on the right to improve stability of shorelining, i.e. doorways cause big issues right now

#!/usr/bin/env python3
# to run on raspberry pi use, add sudo if run into issues with serial: python3 assist_cane_hallway_test.py
from rplidar import RPLidar
import RPi.GPIO as IO
import numpy as np
import time
import serial
import struct
import signal
import sys
import board
import busio
import adafruit_fxos8700 # accel and magnetometer
# import adafruit_fxas21002c # currently don't need gyro
import cane_functions as cf

# stops the motors  called when ctrl-c is hit
def exit_function(signal, frame):
    print('Exiting...')
    p_L.stop()
    p_R.stop()
    lidar.stop()
    lidar.stop_motor()
    time.sleep(2.0)
    lidar.disconnect()
    time.sleep(2.0)
    sys.exit(0)
# intialize exit function
signal.signal(signal.SIGINT, exit_function)

# intialize serial and rplidar
PORT_NAME = '/dev/ttyUSB0'
run_flag = True # starts the program, keeps it running
time.sleep(.5) # rest to start serial
lidar = RPLidar(PORT_NAME)
iterator = lidar.iter_scans(max_buf_meas=120)
time.sleep(.5) # pause to start lidar scanning

# distance and lidar thresholds
hallway_steering_thresh = 950.0 # if any lidar reading less than this, move away from that side
forward_thresh = 1850.0 # only look to turn if less than 2 meters of room ahead
right_thresh = 900.0 # keep the right wall 1m away at all times
right_check_thresh = 2000.0 # always turn right if at least this much space
crash_thresh = 400.0 # if turning into a wall then stop turning
angle_offset = 0.0 #-45.0 # because lidar turned 45 degrees to left
forward_range_low = -5.0+angle_offset # in degrees
forward_range_upper = 5.0+angle_offset # in degrees
left_range_low = 85.0+angle_offset #in degrees
left_range_upper = 95.0+angle_offset #in degrees
right_range_low = -95.0+angle_offset #in degrees
right_range_upper = -85.0+angle_offset #in degrees

# discretized lidar array setup
array_sections = 19 # always have odd value here
num_front_sect = 2 # use the middle section +/- this many sections for checking front collision
array_start = -90.0
array_stop = 90.0
arr_width = (array_stop - array_start)/array_sections
lidar_ang_arr = np.zeros((array_sections,2)) # start then stop angle values
lidar_arr_mean = np.zeros(array_sections) # goes from right to left
distances = np.zeros(array_sections)
for i in range(array_sections):
    start_ang = array_start+i*arr_width
    stop_ang = start_ang + arr_width
    lidar_arr_mean[i] = int((start_ang + stop_ang)/2.0)
    lidar_ang_arr[i,:] = [start_ang+angle_offset,stop_ang+angle_offset]
mid_ind = array_sections//2
lidar_arr_mean -= lidar_arr_mean[mid_ind]
lidar_arr_mean = -1*lidar_arr_mean
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

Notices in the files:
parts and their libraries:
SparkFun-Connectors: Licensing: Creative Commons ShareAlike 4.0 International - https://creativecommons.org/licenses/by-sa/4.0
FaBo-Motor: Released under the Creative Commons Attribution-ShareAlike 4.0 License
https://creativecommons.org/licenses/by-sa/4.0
